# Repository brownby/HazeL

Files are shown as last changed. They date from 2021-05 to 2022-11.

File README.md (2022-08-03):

<p align="center">
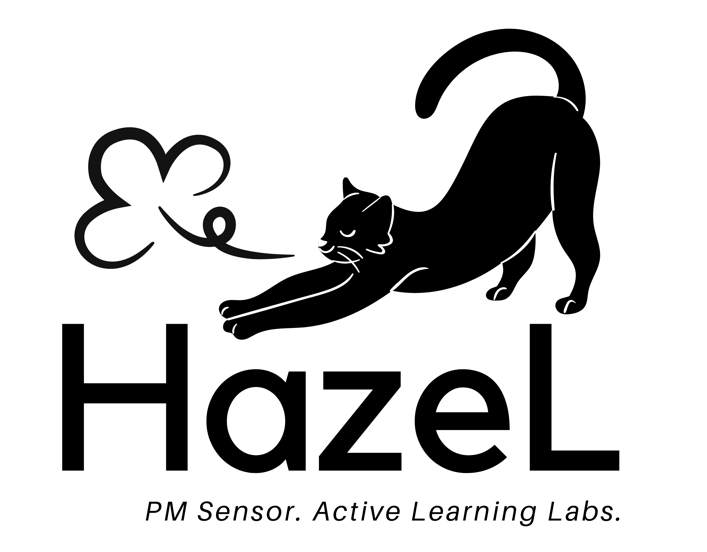
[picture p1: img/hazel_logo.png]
HazeL logo
  
</p>

# HazeL

HazeL is a low-cost, easy to manufacture particulate matter (PM) sensor created for the Harvard University SEAS course ESE6, Introduction to Environmental Science and Engineering. It was designed in response to the need for remote lab activites during the COVID-19 pandemic, but will continue to be used for the foreseeable future. Instead of students needing to share a limited number of expensive sensors, every student is able to collect their own data with their own personal sensor. 

<p align="center">
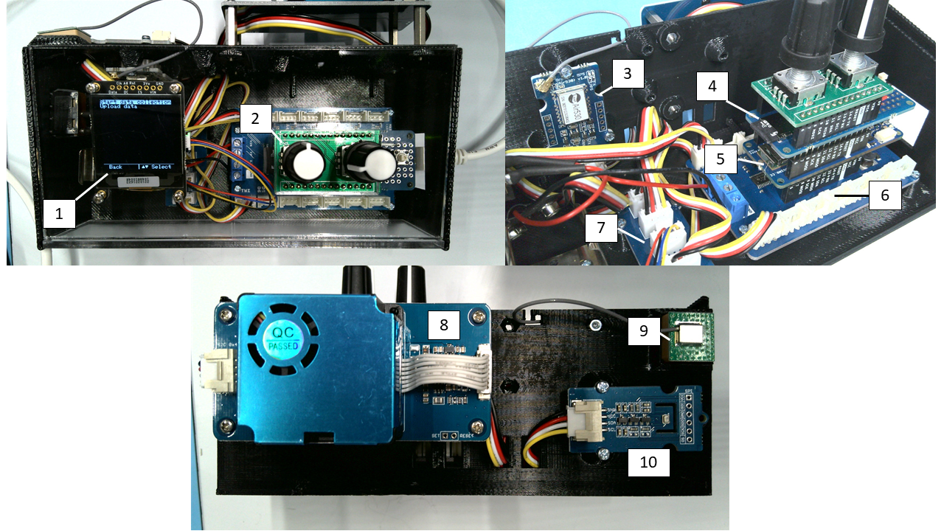
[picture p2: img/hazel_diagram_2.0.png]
HazeL
 
</p>
The components that make up HazeL are, as numbered in the above image:

1. OLED display
2. Rotary encoders mounted on custom PCB
3. GPS module
4. MKR SD shield w/ microSD card inserted
5. Arduino MKR WiFi 1010
6. MKR connector carrier
7. Grove I2C hub
8. Dust sensor
9. GPS antenna
10. Temperature and pressure sensor

All modules and sensors in HazeL use the [Grove connector system](https://www.seeedstudio.com/category/Grove-c-1003.html). You can find links to all of the components of HazeL in the next few sections.

A simplified electrical schematic of HazeL is shown below. **Note:** the level-shifting circuitry present on the MKR connector carrier is abstracted away in this schematic, but remember that Grove devices are 5V logic, while the MKR-series Arduinos are 3.3V logic devices. 

<p align="center">
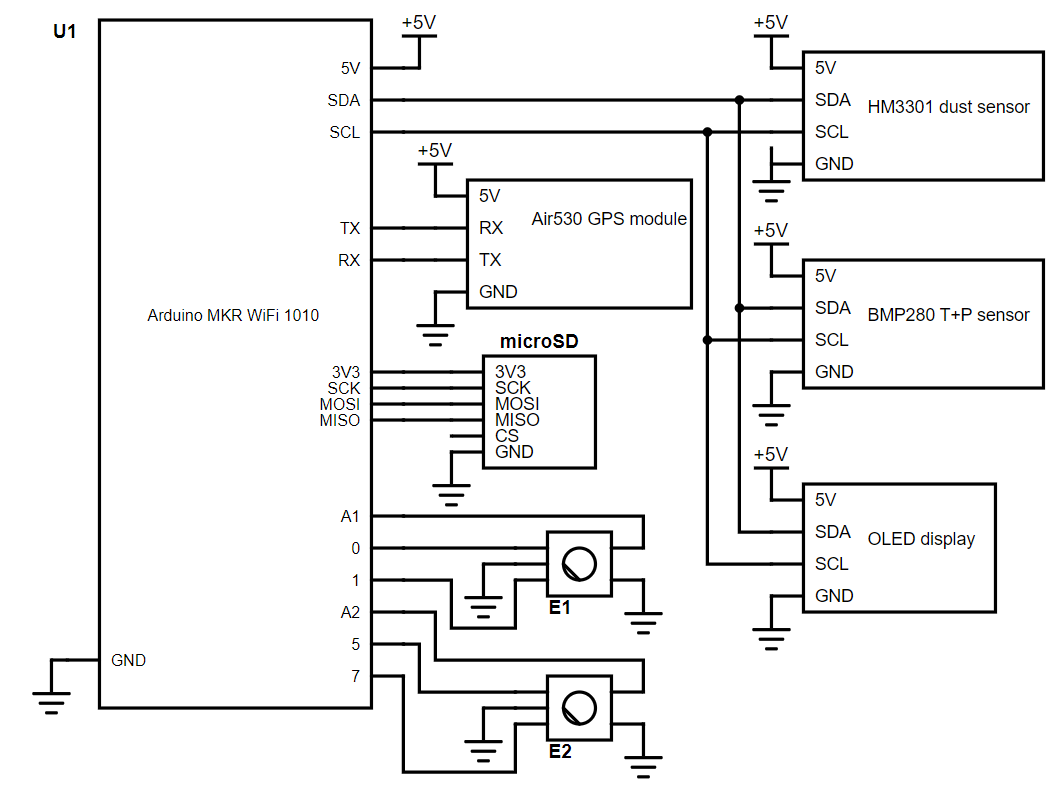
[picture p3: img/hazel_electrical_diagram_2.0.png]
HazeL electrical schematic

</p>

We have open sourced all of our design files in this repository, including the 3D printing files for the [enclosure](enclosure). If you are interested in deploying your own version of HazeL and have any questions beyond those answered by looking through this repository, feel free to reach out to Ben Brown at brown@g.harvard.edu. 

# Device operation

On start-up, HazeL initializes all sensors and modules, then opens the home menu with two options:
```
Start data collection
Upload data
```

For all menus, you use the right knob to scroll up and down, and press the knob to select. The left knob will be used to scroll left and right (when relevant), and can be pressed to go back a menu. 

## Data collection

When you select `Start data collection`, another menu will appear asking you what method you would like to use to timestamp your data:
```
Timestamp method?
_________________
Auto (GPS)
Manual
```

**`Auto (GPS)`**: HazeL will use the GPS module to timestamp data (as well as provide latitude, longitude, and altitude). The first GPS read can take a few minutes - if it takes longer than ten minutes, the read will time out and a message will appear suggesting you enter a timestamp manually. 

**`Manual`**: You will enter a date and time manually using the two knobs (**Note**: the time should be in UTC), at which point HazeL will sync the microcontroller's real-time counter (RTC) peripheral to the time you entered. During data collection, further timestamps will be pulled from the RTC. 

Once an initial timestamp is collected (whether by the GPS or entered by the user), HazeL creates two timestamped files on the SD card that will be used to store data and metadata. The naming convention for the files is:
```
YYMMDD_HHMMSS_data.txt
YYMMDD_HHMMSS_meta.txt
```

Every 2.5 seconds, particulate matter data are collected from the dust sensor and saved in the `data` file. For the list of data that are collected and saved, see the [HM3301 dust sensor section](#hm3301-dust-sensor) below. Each line of the `data` file also starts with the number of milliseconds elapsed since data collection began as well as an ISO8601 UTC timestamp.

Every 10 seconds, a line of metadata is stored in the `meta` file. One line of metadata includes: 
```
ms timer, ISO8601 UTC timestamp, latitude, longitude, altitude, temperature in degrees C, pressure in pascals
```
If the RTC is being used for timestamps (i.e. if `Manual` was selected), the `latitude`, `longitude`, and `altitude` entries will be empty. The RTC may also be used if you selected `Auto (GPS)`, but only in cases where a GPS read takes longer than 5 seconds. The `ms timer` value is the number of milliseconds elapsed since data collection began. This value, as well as the timestamp, will match on a line where both data and metadata are collected, allowing for synchronization of the two files in post-processing. 

As data are being saved to the SD card, they are also being sent over USB to allow for capturing a livestream of data. Livestreamed metadata lines begin with a `#` to differentiate them from data. 

The OLED display will also show data as it is collected, specifically the count/0.1L of >0.3um particles. The current date and time (in UTC) are shown at the bottom of the display, as well as the source of the timestamp (either `RTC` or `GPS`):

```
>0.3um:

400
count/0.1L

1/13/2022 18:24 (GPS)
```

When you are done collecting data, you can press the back button to return to the previous menu, or simply turn off the device.

**Note on GPS:** 
As mentioned above, depending on the strength of GPS signals, the first GPS read may take a few minutes, during which time the OLED will read:
```
Reading GPS...

(First GPS read
may take a
few minutes)
```
HazeL will wait up to 10 minutes for a successful first GPS read before it starts collecting data. If the initial GPS read takes longer than 10 minutes, it is recommended to enter a timestamp manually instead. 

The RTC is synced to the GPS on every successful GPS read. When a GPS read is unsuccessful (i.e. takes longer than 5 seconds), HazeL will automatically pull the timestamp from the RTC instead. This should allow the RTC to fill in gaps in GPS reads caused by spotty GPS signals. As noted above, any metadata line that uses the RTC will have blank latitude, longitude, and altitude entries.

## Uploading data

### Using the [HazeL Data Downloader](https://hazeldownload.com/) (preferred)

Go to [hazeldownload.com](https://hazeldownload.com/) and follow the directions there to connect your device. The Downloader will then show a list of all the files on the SD card, and you can select the ones you would like to download and click `Download`. That's it!

### Using [Scripts](scripts)

When you select `Upload data`, a new menu will appear with a list of all of the data and metadata files stored on the SD card in reverse chronological order. For example, if you collected data three times on `1/13/22`, once at `9:24:29`, once at `13:40:12`, and once at `18:08:57`, the screen would look like this:

```
Select a file
___________________
221301_180857_meta
221301_180857_data
221301_134012_meta
221301_134012_data
221301_092429_meta
221301_092429_data
```

Scroll to the file you would like to upload with the right knob, and select it by pressing the right knob. Once you select a file, the data from the file is sent over USB, and the screen will display:

```
Uploading
<file_name>
via serial port
```

In order to save data to your computer, you must use one of the data download scripts in the [scripts](scripts) folder of this repository. You can find more info on how to use the scripts in the README in that folder. 

# HazeL components

## Arduino MKR WiFi 1010

The [Arduino MKR WiFi 1010](https://store-usa.arduino.cc/products/arduino-mkr-wifi-1010) serves as the brains of HazeL, mounted on the [MKR Connector Carrier](https://store.arduino.cc/usa/arduino-mkr-connector-carrier). The [MKR SD Proto Shield](https://store.arduino.cc/usa/mkr-sd-proto-shield) is mounted onto the MKR WiFi 1010, which provides a microSD card slot.

The Arduino code can be found in [HazeL.ino](src/HazeL.ino). While only tested on the MKR1000 and MKR WiFi 1010, it should be compatible with most SAMD21-based Arduinos (**note:** this is not true of the code on the thingspeak branch, which takes advantage of the WiFi capabilities of the MKR1000 and MKR WiFi 1010 to create an IoT enabled version of HazeL). Feel free to submit an issue if you encounter issues on other platforms. 

This repository is structured as a [PlatformIO](https://platformio.org/) project, if you'd like to use it within the Arduino IDE instead, move the contents of the [src](src) and [include](include) folders into a folder entitled `HazeL`, and open `HazeL.ino` in the Arduino IDE. 

## Other modules

### [HM3301 dust sensor](https://www.seeedstudio.com/Grove-Laser-PM2-5-Sensor-HM3301.html)

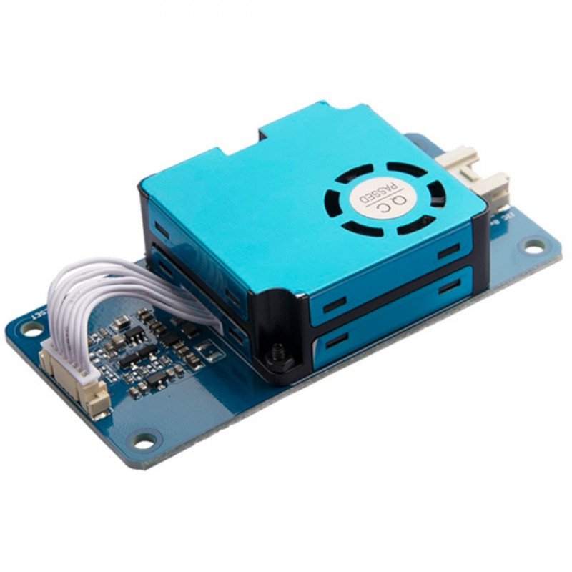
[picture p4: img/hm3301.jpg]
HM3301 dust sensor


The HM3301 is the dust sensor used in HazeL. It returns the following data, all of which are saved on each data line in `data.txt` in the order shown below:

|Datum|Units|
|:---:|:---:|
|PM1.0 (standard)&#8224;|&#956;g/m<sup>3</sup>|
|PM2.5 (standard)&#8224;|&#956;g/m<sup>3</sup>|
|PM10.0 (standard)&#8224;|&#956;g/m<sup>3</sup>|
|PM1.0 (atmospheric)|&#956;g/m<sup>3</sup>|
|PM2.5 (atmospheric)|&#956;g/m<sup>3</sup>|
|PM10.0 (atmospheric)|&#956;g/m<sup>3</sup>|
|>0.3 &#956;m|Particle count/0.1L|
|>0.5 &#956;m|Particle count/0.1L|
|>1.0 &#956;m|Particle count/0.1L|
|>2.5 &#956;m|Particle count/0.1L|
|>5.0 &#956;m|Particle count/0.1L|nmjjjjjjjjjjjjjjjjjjjjjjjjj
|>10.0 &#956;m|Particle count/0.1L|

The HM3301 communicates with the Arduino over I2C, using a custom library written for HazeL (see [HM3301.cpp](src/HM3301.cpp) and [HM3301.h](include/HM3301.h)).

It should be mounted to the outside of the enclosure, with sufficient clearance to allow for unobstructed airflow into the inlet.

&#8224;These data are not saved to the SD card in the current version of HazeL.

### [BMP280 temperature and pressure sensor](https://www.seeedstudio.com/Grove-Barometer-Sensor-BMP280.html)

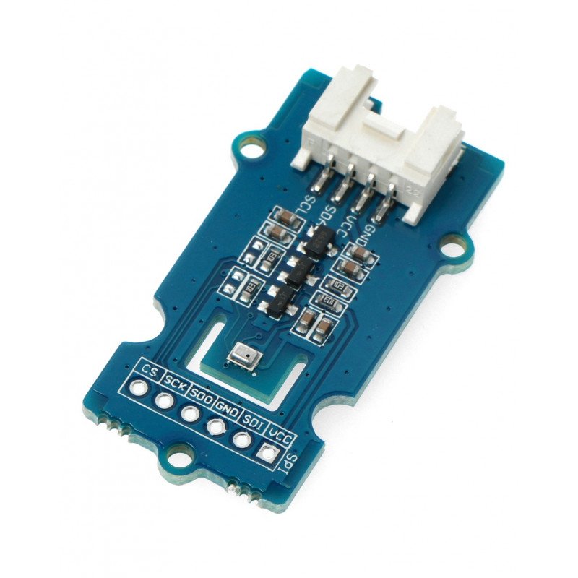
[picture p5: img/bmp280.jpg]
BMP280 temperature and pressure sensor


The BMP280 is a low-cost temperature sensor and barometer that communicates over I2C, using a slightly modified version of Seeed's [library](https://github.com/Seeed-Studio/Grove_BMP280) that can be found [here](https://github.com/brownby/Grove_BMP280). 

It should be mounted on the outside of the enclosure as well, close to the HM3301.

### [Air530 GPS module](https://www.seeedstudio.com/Grove-GPS-Air530-p-4584.html)

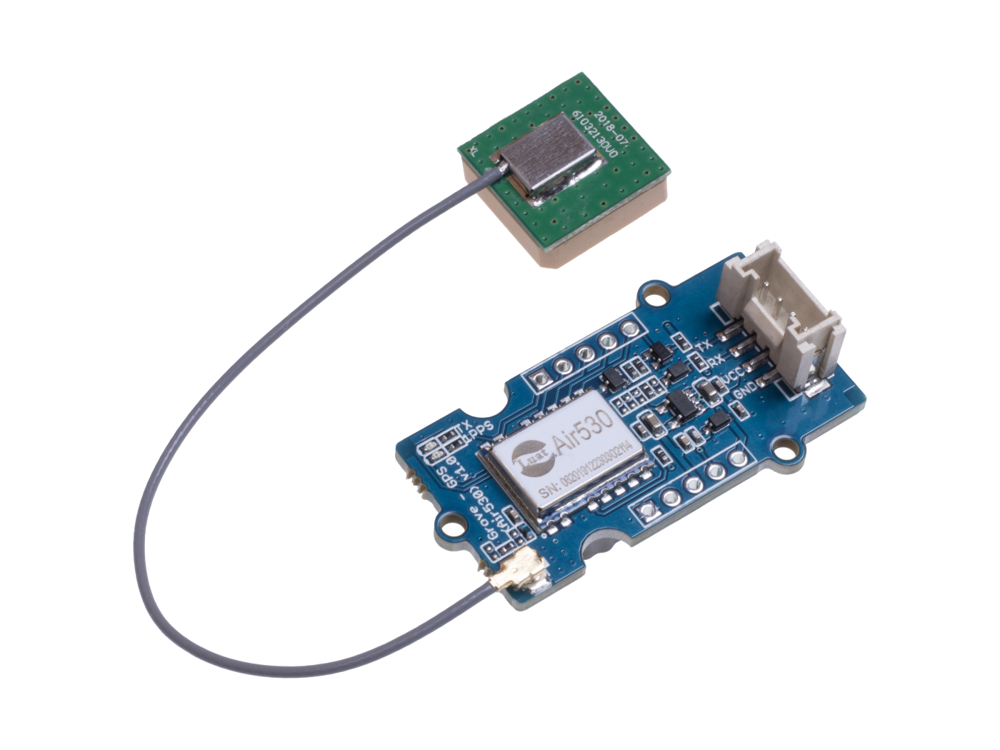
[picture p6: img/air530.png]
Air530 GPS module


The Air530 is low-cost GPS module that comes with a small antenna. It communicates over UART, currently just using functions inside of [HazeL.ino](src/HazeL.ino), but I will likely break this out into a separate library in the future. The GPS readings are decoded using the [TinyGPS++ library](http://arduiniana.org/libraries/tinygpsplus/) by Mikal Hart.

### [SSD1327 OLED display](https://www.adafruit.com/product/4741)

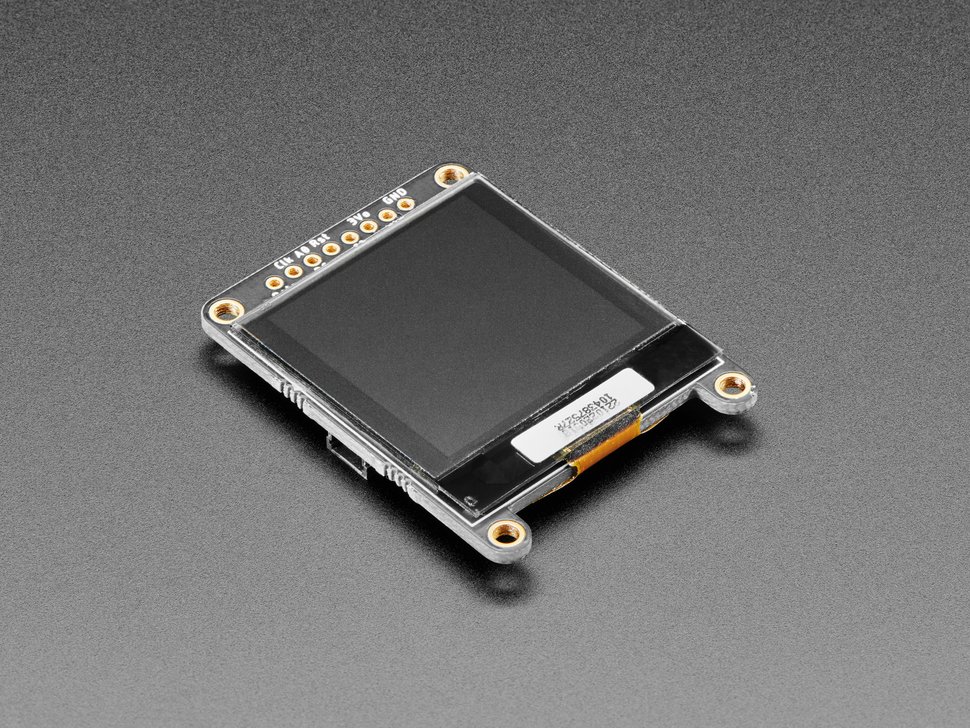
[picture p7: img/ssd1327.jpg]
SSD1327 OLED display


The SSD1327 is a 1.5" 128x128 grayscale OLED display. The display is used to display data to the user, as well as menus for users to navigate. The OLED communicates over I2C using the [Adafruit_SSD1327 library](https://github.com/adafruit/Adafruit_SSD1327).

### [I2C hub](https://www.seeedstudio.com/Grove-I2C-Hub.html)

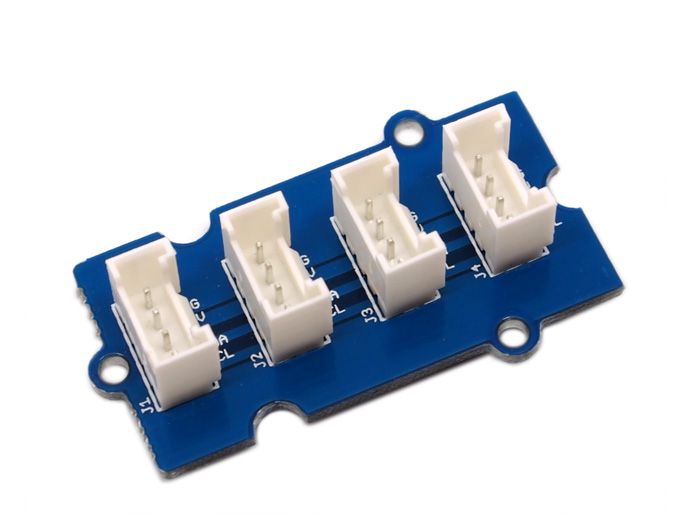
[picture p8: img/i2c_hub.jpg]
Grove I2C hub


The Grove I2C hub was used to connect the I2C devices (dust sensor, T+P sensor, and OLED display) to the MKR1000's I2C bus.

### [Encoders](https://www.digikey.com/en/products/detail/bourns-inc/PEC11R-4220F-S0024/4499660)

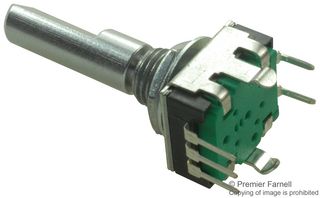
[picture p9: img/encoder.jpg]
Rotary encoder


These encoders are used as the knobs and buttons to interact with HazeL. They are mounted on a custom PCB. 

# Serial Commands

**New with HazeL 3.0!**

HazeL will now respond to two serial commands:

`ls` - HazeL will respond with a list of all files on the SD card, followed by an [`EOT` character](https://en.wikipedia.org/wiki/End-of-Transmission_character)

`dl <filename1> <filename2> ...` - HazeL will send the contents of each `filename` send to it, one-by-one. Each file will end with an [`ETX` character](https://en.wikipedia.org/wiki/End-of-Text_character), and once all the files are sent HazeL will send an `EOT` character.

These serial commands are what enables the [HazeL Data Downloader](https://hazeldownload.com/) to operate.

# The Meaning of "HazeL"

HazeL is named after Hazel the cat, shown below, who is a very good girl. (It can also mean Haze Laser sensor, but we all know it was for the cat). 

<p align="center">
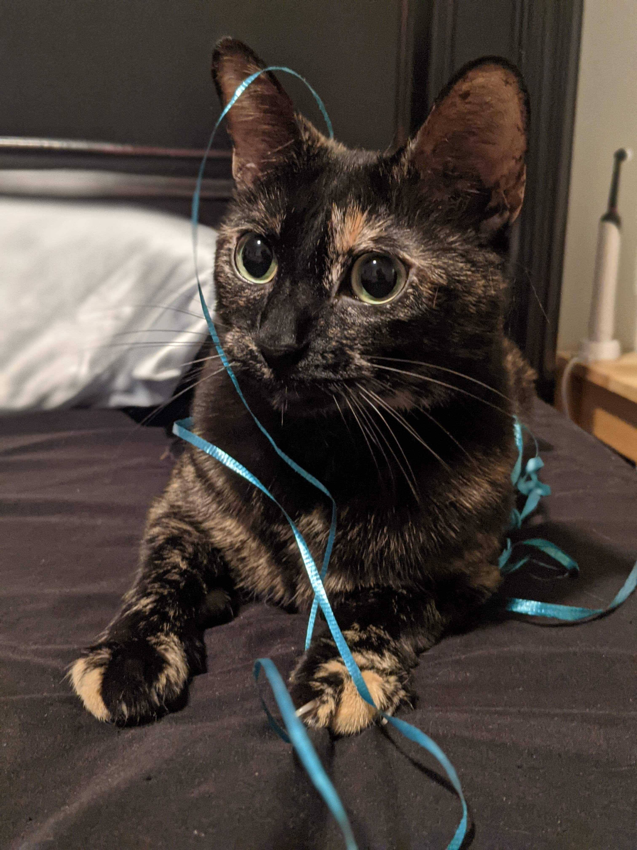
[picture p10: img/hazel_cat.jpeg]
Hazel the cat
  
</p>

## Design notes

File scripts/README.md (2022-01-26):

# Data download scripts

This directory contains two scripts that can be used for capturing the data stream from a HazeL device when it's connected to a computer via USB. When HazeL saves data to the SD card, it also send that data over the USB port if there is a device connected to it. The scripts can be used to capture this live data stream from HazeL, or to capture data from an uploaded file.

## Script usage

### logging.sh

On Mac, data can be captured using the bash script `logging.sh`. After downloading the script, open the terminal and navigate to the directory where you downloaded it. Run the command
```
chmod 755 logging.sh
```
to make it an executable (you only need to run this once). 

Before running the script, plug a HazeL into your computer using the USB micro-B port on the Arduino MKR WiFi 1010. Then, run the script:
```
./logging.sh
```
The script will read the first line sent from the HazeL and use that as the file name. When used properly, this should mean the file on your machine has the same name as the file on HazeL's SD card. 

The script should be terminated with `Ctrl+C` and re-run when downloading a new file. 

### readCOM.ps1

On Windows, data can be captured using the PowerShell script `readCOM.ps1`. After downloading the script, move it to the directory where you would like to store data. 

Before running the script, plug a HazeL into your computer using the USB micro-B port on the Arduino MKR WiFi 1010. Then, right click on the script and select "Run with PowerShell". 

The script will read the first line sent from the HazeL and use that as the file name. When used properly, this should mean the file on your machine has the same name as the file on HazeL's SD card. 

After a file has been downloaded, the script continues running and waits for another file to be uploaded. You can terminate execution by closing the PowerShell window. 

**Note:** if the script will not run by right clicking, you may need to adjust your system's PowerShell permissions. This can be done using the `Set-ExecutionPolicy` cmdlet, more information [here](https://docs.microsoft.com/en-us/powershell/module/microsoft.powershell.core/about/about_execution_policies?view=powershell-7.1)

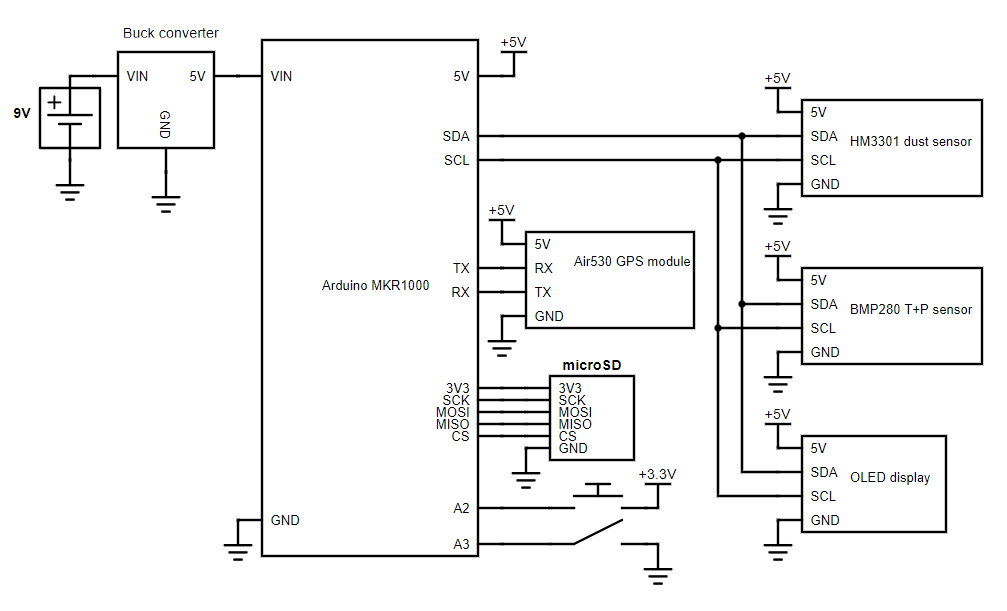
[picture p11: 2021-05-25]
img/hazel_electrical_diagram.png

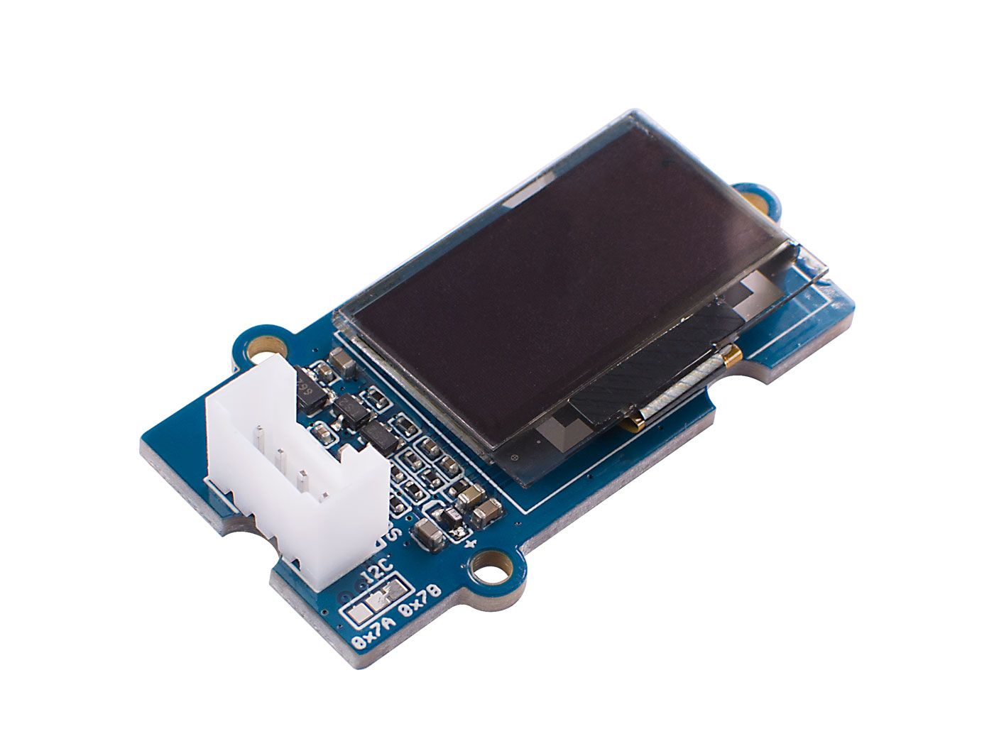
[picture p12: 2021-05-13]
img/ssd1315.jpg

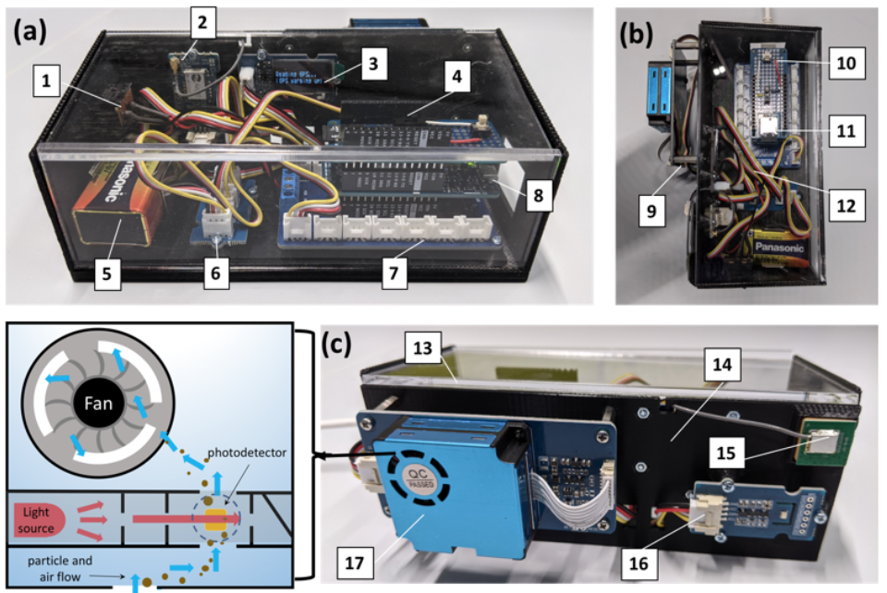
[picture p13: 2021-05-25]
img/hazel_diagram.png

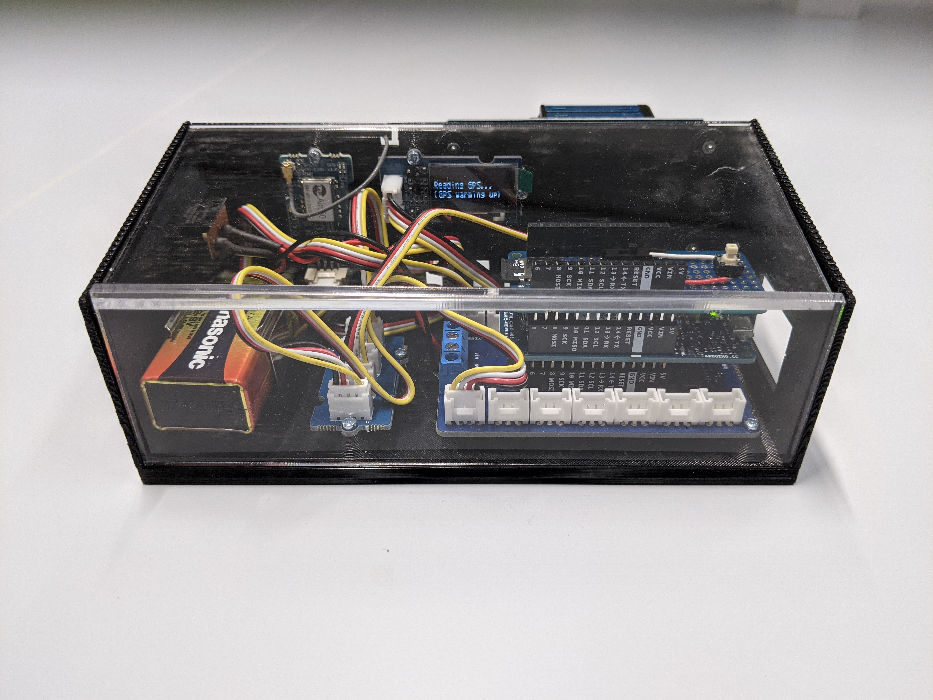
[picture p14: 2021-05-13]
img/hazel_front.jpg

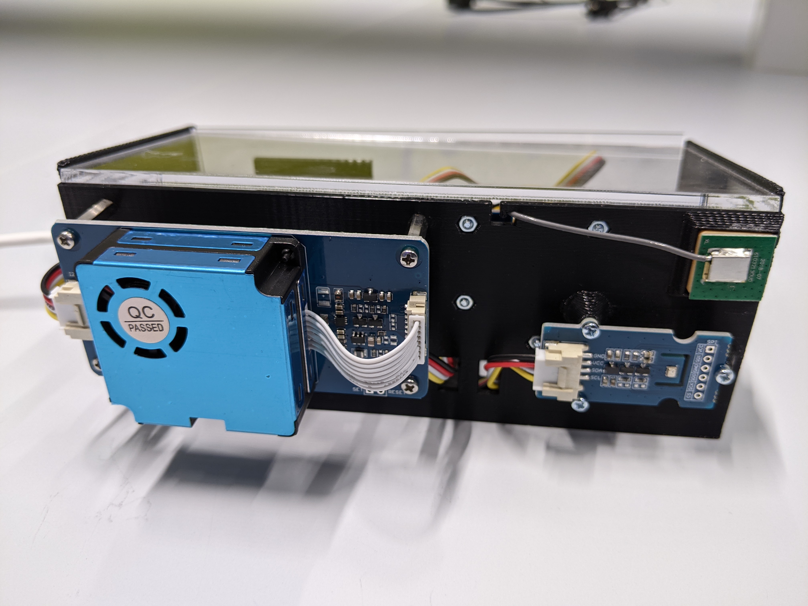
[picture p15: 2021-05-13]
img/hazel_back.jpg

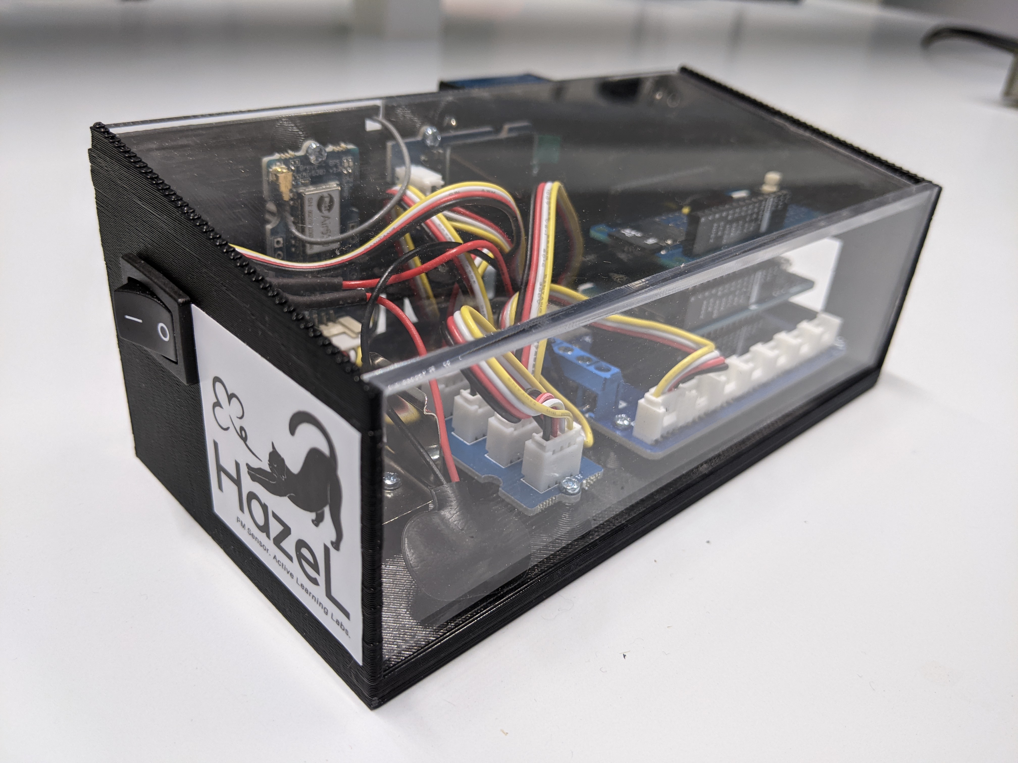
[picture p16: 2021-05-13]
img/hazel_side.jpg

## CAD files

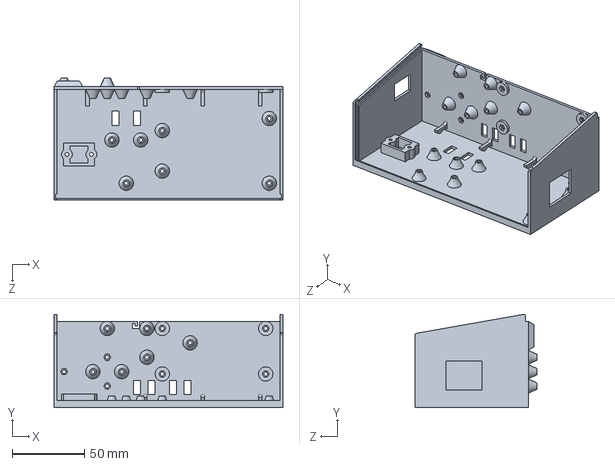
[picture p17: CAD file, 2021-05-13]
enclosure/ES6 Mount v6.SLDPRT
159.0 x 64.8 x 84.6 mm

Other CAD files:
enclosure/ES6 Mount v6.STL

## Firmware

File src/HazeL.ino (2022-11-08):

/*
 * HazeL
 * Benjamin Y. Brown
 */

#include <SPI.h>
#include <Wire.h>
#include "HM3301.h"

// Make sure you have these five libraries installed in Documents/Arduino/libraries
#include <Adafruit_I2CDevice.h>
#include <Adafruit_GFX.h>
#include <Adafruit_SSD1327.h>
#include <Encoder.h>
#include "SdFat.h"
#include <TinyGPS++.h>
#include <TimeLib.h>
#include <RTCZero.h>
#include "Seeed_BMP280.h"

#define SAMP_TIME 2500 // number of ms between sensor readings
#define BLINK_TIME 30 // time in ms between LED blinks on successful write to SD
#define GPS_TIME 10000 // time between GPS reads
#define GPS_TIMEOUT 5000 // number of ms before GPS read times out
#define GPS_FIRST_TIMEOUT 600000 // number of ms before first GPS read times out
#define BLINK_CNT 3 // number of times to blink LED on successful write
#define SD_CS_PIN 4 // CS pin of SD card, 4 on SD MKR proto shield
#define CUR_YEAR 2022 // for GPS first fix error checking
#define OLED_RESET -1
#define SCREEN_ADDRESS 0x3D
#define SCREEN_WIDTH 128
#define SCREEN_HEIGHT 128
#define ENC_RIGHT_BUTTON A1
#define ENC_RIGHT_A 0
#define ENC_RIGHT_B 1
#define ENC_LEFT_BUTTON A2
#define ENC_LEFT_A 5
#define ENC_LEFT_B 7
#define MENU_UPDATE_TIME 100 // milliseconds between menu updates
// #define DEBUG_PRINT

HM3301 dustSensor;
BMP280 TPSensor;

SdFat SD;
File dataFile;
File metaFile;
char dataFileName[23]; // YYMMDD_HHMMSS_data.txt
char metaFileName[23]; // YYMMDD_HHMMSS_meta.txt
char * fileList; // list of files on SD card
bool fileListAlloc = false; // variable for tracking if fileList is malloc'd to avoid memory leaks
uint32_t fileCount = 0; // number of files on SD card
char fileToUpload[30];

TinyGPSPlus gps;
bool timestampFlag = false;
bool gpsAwake = true;
bool gpsDisplayFail = false;

int utcYear;
int utcMonth;
int utcDay;
int utcHour;
int utcMinute;
int utcSecond;
double latitude;
double longitude;
double altitude;

time_t prevTimeStamp = 0;
uint8_t manualMonth = 1;
uint8_t manualDay = 1;
uint16_t manualYear = CUR_YEAR;
uint8_t manualHour = 0;
uint8_t manualMinute = 0;
bool manualTimeEntry = false; // false means use GPS
bool rtcSet = false; // flag to indicate if RTC is set or not
RTCZero rtc;

Adafruit_SSD1327 display(SCREEN_WIDTH, SCREEN_HEIGHT, &Wire, OLED_RESET);

Encoder encRight(ENC_RIGHT_B, ENC_RIGHT_A);
Encoder encLeft(ENC_LEFT_B, ENC_LEFT_A);
long encRightOldPosition = 0;
long encLeftOldPosition = 0;

unsigned long prevSampMillis = 0;
unsigned long prevLedMillis = 0;
unsigned long prevGpsMillis = 0;
unsigned long prevMenuMillis = 0;
unsigned long dataStartMillis = 0; // millis() when data collection began
unsigned long curMillis;

volatile bool encRightButtonFlag = false;
volatile bool encRightButtonISREn = false;
volatile bool encLeftButtonFlag = false;
volatile bool encLeftButtonISREn = false;

bool ledFlag = false;
uint8_t ledCount = 0;

bool firstMeasurementFlag = false;

// state = 0 navigating menu
// state = 2 collecting data
// state = 3 uploading data
uint8_t state = 0;
uint8_t prevState = 0;

// page = 0 two choice menu, collect data and upload data
// page = 1 time entry choice menu -> two choices enter timestamp or get from GPS
// page = 2 entering date
// page = 3 entering time
// page = 4 viewing SD card files
// page = 5 data collection screen
uint8_t page = 0;
uint8_t prevPage = 0;
int16_t currentVertMenuSelection = 0;
int16_t currentHoriMenuSelection = 0;
int16_t prevVertMenuSelection = 0;
uint8_t scroll = 0; // count number of times SD page has been scrolled

void setup() {
  // initialize Serial port
  Serial.begin(115200);

  // intialize comms with GPS module
  Serial1.begin(9600);

  // Initialize I2C bus
  Wire.begin();

  // Initialize comms with OLED display
  display.begin(SCREEN_ADDRESS);

  display.clearDisplay();
  updateDisplay("Initializing...", 40, false);
  display.display();
  delay(2500);
  #ifdef DEBUG_PRINT
  Serial.println("Initializing...");
  #endif

  // Set relevant pin modes
  pinMode(LED_BUILTIN, OUTPUT);
  pinMode(SD_CS_PIN, OUTPUT);
  pinMode(ENC_RIGHT_BUTTON, INPUT_PULLUP);
  pinMode(ENC_LEFT_BUTTON, INPUT_PULLUP);

  #ifdef DEBUG_PRINT
  Serial.println("Initialize SD");
  #endif
  display.clearDisplay();
  updateDisplay("Checking SD", 40, false);
  display.display();
  delay(2500);

  // Initialize SD card communication
  if(!SD.begin(SD_CS_PIN))
  {
    #ifdef DEBUG_PRINT
    Serial.println("Card failed");
    #endif
    display.clearDisplay();
    updateDisplay("SD card failed", 32, false);
    updateDisplay("Reset device", 48, false);
    display.display();
    while(true);
  }
  else
  {
    #ifdef DEBUG_PRINT
    Serial.println("Card initialized successfully");
    #endif
    display.clearDisplay();
    updateDisplay("SD card detected", 40, false);
    display.display();
  }
  delay(2500);

  // Initialize dust sensor
  if(!dustSensor.begin())
  {
    #ifdef DEBUG_PRINT
    Serial.println("Failed to initialize dust sensor");
    #endif
    display.clearDisplay();
    updateDisplay("Dust sensor init failed", 32, false);
    updateDisplay("Reset device", 48, false);
    display.display();
    while(true);
  }

  TPSensor.init();

  // Put GPS to sleep to start
  if(gpsAwake)
  {
    toggleGps();
  }

  // Begin RTC
  rtc.begin();

  // Attach ISR for flipping buttonFlag when button is pressed
  attachInterrupt(digitalPinToInterrupt(ENC_RIGHT_BUTTON), encRightButtonISR, FALLING);
  attachInterrupt(digitalPinToInterrupt(ENC_LEFT_BUTTON), encLeftButtonISR, FALLING);

  // enable button ISR
  encRightButtonISREn = true;
  encLeftButtonISREn = true;

  // set initial state to menu navigation
  state = 0;
}

void loop() {
  // check number of milliseconds since Arduino was turned on
  curMillis = millis();

  // display the current page
  displayPage(page);

  if(state == 0) // Navigating menus
  {
    // update the current menu selection
    updateMenuSelection();

    // Check for serial commands
    String msg = "";
    while (Serial.available() > 0)
    {
      char c = Serial.read();
      msg += c;
      // End of command
      if (c == '\n')
      {
        String cmd = String(msg[0]) + String(msg[1]);

        // Get list of all files, if not already created
        if (!fileListAlloc)
        {
          getFileList();
        }
        char allFiles[fileCount][30];
        memcpy(allFiles, fileList, sizeof(allFiles));

        // Send list of files
        if (cmd == "ls")
        {
          #ifdef DEBUG_PRINT
          Serial.println("ls command");
          #endif
          for (int i = 0; i < fileCount; i++)
          {
            Serial.print(allFiles[i]);
            Serial.print('\n');
          }
          Serial.print('\x04');
        }
        // Download files
        else if (cmd == "dl")
        {
          #ifdef DEBUG_PRINT
          Serial.println("dl command");
          #endif

          // Remove command and space from the msg string
          msg = msg.substring(3);

          #ifdef DEBUG_PRINT
          Serial.print("dl args: "); Serial.println(msg);
          #endif

          // Create an array for storing all the files in the argument
          char filesToDownload[fileCount][30];
          String fileName = "";
          uint32_t downloadCount = 0;
          int i = 0;

          // Construct array of files to download
          while (i < msg.length())
          {
            // Encountered a space, add fileName to array
            if (msg[i] == ' ' || msg[i] == '\n')
            {
              #ifdef DEBUG_PRINT
              Serial.print("fileName: "); Serial.println(fileName);
              #endif

              strcpy(filesToDownload[downloadCount], fileName.c_str());

              downloadCount++;

              // Reset fileName
              fileName = "";
            }
            else
            {
              fileName += msg[i];
            }
            i++;
          }
          #ifdef DEBUG_PRINT
          Serial.print("downloadCount: "); Serial.println(downloadCount);
          #endif

          // Upload each file one by one, terminate with end ETX character
          for (int i = 0; i < downloadCount; i++)
          {
            #ifdef DEBUG_PRINT
            Serial.print("Uploading file: "); Serial.println(filesToDownload[i]);
            #endif

            uploadSerial(filesToDownload[i], 100);
            Serial.print('\x03');
          }
          Serial.print('\x04');
        }

        // If we're currently on the page for viewing the files on the SD, don't free() fileList
        if (page != 4)
        {
          free(fileList);
          fileListAlloc = false;
        }
      }
    }

    if(encRightButtonFlag) // select button has been pressed
    {
      if(page == 0) // initial menu
      {
        if(currentVertMenuSelection == 0)
        {
          page = 1; // go to time entry choice page
        }
        else if(currentVertMenuSelection == 1) // upload data
        {
          prevState = state;
          page = 4; // go to page for viewing SD card files
          scroll = 0; // start at the beginning of the file list
          #ifdef DEBUG_PRINT
          Serial.println("\nSD card contents from SD.ls():");
          SD.ls(LS_R);
          Serial.println();
          #endif

          // Create file list, if not already created
          if (!fileListAlloc)
          {
            getFileList();
          }
        }
      }
      else if (page == 1) // time entry method
      {
        if(currentVertMenuSelection == 0) // Use GPS for time stamp
        {
          manualTimeEntry = false;
          createDataFiles(); // create the names for the data and gps files for data collection
          // State and page are set from within createDataFiles() so that I can set it to different things on success and failure
        }
        else if(currentVertMenuSelection == 1) // Use manual entry + RTC
        {
          page = 2; // enter date
          if(rtcSet)
          {
            manualDay = rtc.getDay();
            manualHour = rtc.getHours();
            manualMinute = rtc.getMinutes();
            manualMonth = rtc.getMonth();
            manualYear = rtc.getYear();
          }
        }
      }
      else if (page == 2)
      {
        page = 3; // enter time
      }
      else if (page == 3)
      {
        #ifdef DEBUG_PRINT
        Serial.print("Timestamp set as: ");
        Serial.print(manualMonth);
        Serial.print('/');
        Serial.print(manualDay);
        Serial.print('/');
        Serial.print(manualYear);
        Serial.print(' ');
        if(manualHour < 10) Serial.print('0');
        Serial.print(manualHour);
        Serial.print(':');
        if(manualMinute < 10) Serial.print('0');
        Serial.println(manualMinute);
        #endif

        // set RTC
        rtc.setDate(manualDay, manualMonth, manualYear % 100); // year is saved as an offset from 2000
        rtc.setTime(manualHour, manualMinute, 0);

        if(!rtcSet) rtcSet = true;
        
        manualTimeEntry = true; // flag to indicate that RTC is being used for time stamps, not GPS
        createDataFiles();
        // State and page are set from within createDataFiles() so that I can set it to different things on success and failure
      }
      else if(page == 4)
      {
        // save fileToUpload before uploadSerial is called on it
        memcpy(fileToUpload, fileList + currentVertMenuSelection*30, sizeof(fileToUpload));
        prevState = state;
        state = 3;
      }
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

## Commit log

2020-10-28 Updated to use I2C dust sensor
2020-10-28 Sleep GPS module between sample updates
2020-11-06 Removed print statements
2020-11-07 Updated debug print statements
2020-11-12 client.print() one character at time
2020-11-16 Using INPUT_PULLDOWN instead of physical resistor
2020-11-18 Removed debug print statements
2020-12-18 Moved dust sensor to separate library
2020-12-18 Added temperature sensor
2020-12-18 Print data in single line instead
2021-01-16 Turn off debug print statements
2021-01-17 Turned off debug print statements
2021-01-17 Turned off/removed some debug prints
2021-05-13 Add 3D printing files for enclosure
    [ES6 Mount v6.SLDPRT, ES6 Mount v6.STL]
2021-12-07 Update default board to MKR WiFi 1010
2021-12-14 Update currentVertMenuSelection when horizontal changes
2021-12-14 Shift around some debug print statements
2021-12-14 Fix platform and framework versions for stability
2022-01-03 Small pinout changes for encoder PCB routing
2022-01-03 Moved encoder button pins to avoid built-in LED
2022-01-04 Finalize encoder pinout for PCB routing
2022-01-22 Remove debug print statement
2022-07-31 Fixed dl command implementation, added debug prints
